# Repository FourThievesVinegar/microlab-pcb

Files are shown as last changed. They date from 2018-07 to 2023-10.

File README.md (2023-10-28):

# FTVC Microlab PCB

## NOTE: This project is deprecated. [The new version of the Microlab](https://github.com/FourThievesVinegar/solderless-microlab) uses a Raspberry Pi.

Four Thieves Vinegar Micro Lab

This is the printed circuit board hardware component for controlling the Four Thieves Vinegar Collective's Apothecary Microlab. It was built with Altium Designer v15 and sits mezzanine to the Raspberry Pi Zero.

## Building

To build your own Microlab PCB follow these guides:

[Ordering the PCB](docs/order-pcb.md)

[Ordering the PCB Components](docs/order-pcb-components.md)

## Interfaces

The PCB provides the following interfaces:

* 2 x 12 V Stepper motors
* 4 x Buttons for stepper motor control
* 4 x Limit switches
* 1 x DC motor controller (PWM)
* 3 x Relays
* N x DS18B20 temperature probes
* 2 x Raspberry Pi GPIO

## Electrical

### Power

The PCB is powered by a 12 VDC power brick. It will supply power to the Raspberry Pi Zero, stepper motors, stirrer motor, and temperature probes.

The power connector is a standard 2.10mm ID, 5.50mm OD centre-positive barrel jack connector (PJ-037AH).

Power consumption has yet to be measured.

### Stepper Motors

Drives two bipolar (four-wire) stepper motors with 12 V at 1.2 A max.

Stepper motor driver IC: TB6612FNG.

### Buttons and Limit Switches

Active-high. Includes pull-down resistors and debounce RC filters.

### DC Motor Controller

Supplies 12 VDC at 2 A max. Connected to a PWM pin on the Pi.

### Relays

Rated for 250VAC, 125VDC at 10 A max.

**WARNING:** If you are switching main's powered devices, be careful not to touch the exposed leads on the bottom of the PCB.

### Temperature Probes

Supports any number of DS18B20 temperature probes. Connected to the 1-wire pin on the Pi and includes the data-line pull-up resistor.

### Pi GPIO Pins

Two Pi GPIO pins, BCM0 (pin 27) and BCM1 (pin 28) are exposed along with 5, 12, 3.3 V and GND on a six pin header.

## Mechanical

The PCB is 100 mm x 50 mm with rounded corners.

The three M2.5 mounting holes are concentric with the Pi's. They are drilled to 2.75 mm diameter and provide 6 mm diameter clearance. The centre-to-centre horizontal and vertical distance is 58 mm and 23 mm. The holes' centres are 3.5 mm from their board edge.

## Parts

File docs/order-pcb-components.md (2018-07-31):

# Ordering the PCB Components

This document describes how to order the electrical components for the Apothecary Microlab PCB.

## Info

Cost is USD $30 - $35 + shipping from Digi-Key and takes one to two days to ship within North America.

Includes parts for one Microlab PCB. If you'd like to assemble more, multiply the quantities in the spreadsheet.

## Steps

### Download the BOM

Git clone or download this repository onto your machine.

Alternatively, you can just download the [outputs/microlab-BOM.xls](../outputs/microlab-BOM.xls) file directly from GitHub.

### Create a Digi-Key account

Go to [digikey.com](https://www.digikey.com/) and select your country / region on the top right.

Register to create an account.

### Upload the BOM

Once logged in, view your shopping cart on the top right.

Upload the microlab-BOM.xls file to the shopping cart.

Set the first part record to row two:

Digi-Key first record

Scroll to the right and assign the last three columns of the table to "Digi-Key Part Number", "Customer Reference" and "Quantity":

Digi-Key column options

Click "Add to new cart" and allow it to process your request.

### Order the parts

Review your cart and press the "Checkout" button. Enter your address and payment info.

Place your order, and you are done!

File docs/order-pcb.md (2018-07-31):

# Ordering the PCB

This document describes how to order the Apothecary Microlab PCB to be manufactured.

## Info

Cost is USD $2 + $20 shipping from JLC PCB and takes six days to manufacture and ship to North America.

Includes 10 Microlab PCBs.

## Steps

### Prepare the Gerbers

Git clone or download this repository onto your machine.

Zip all the files in the [outputs/gerbers](../outputs/gerbers) directory into a single archive. Ensure the files are at the root of the archive and not inside a sub-directory.

### Create a JLC PCB account

Go to [jlcpcb.com](https://jlcpcb.com/) and sign up for an account. We use them because they have a special offer of $2 for 10 PCBs and have been tested.

### Upload Gerber files

On the home page, select "Quote Now" for a 2-layer PCB.

Press "Add your gerber file" and upload the .zip file you created. After a short time, it will show a rendering of the PCB.

_Note:_ The bottom side of the render will be mirrored on the website, but not on the real PCBs.

Leave the PCB options on their defaults:

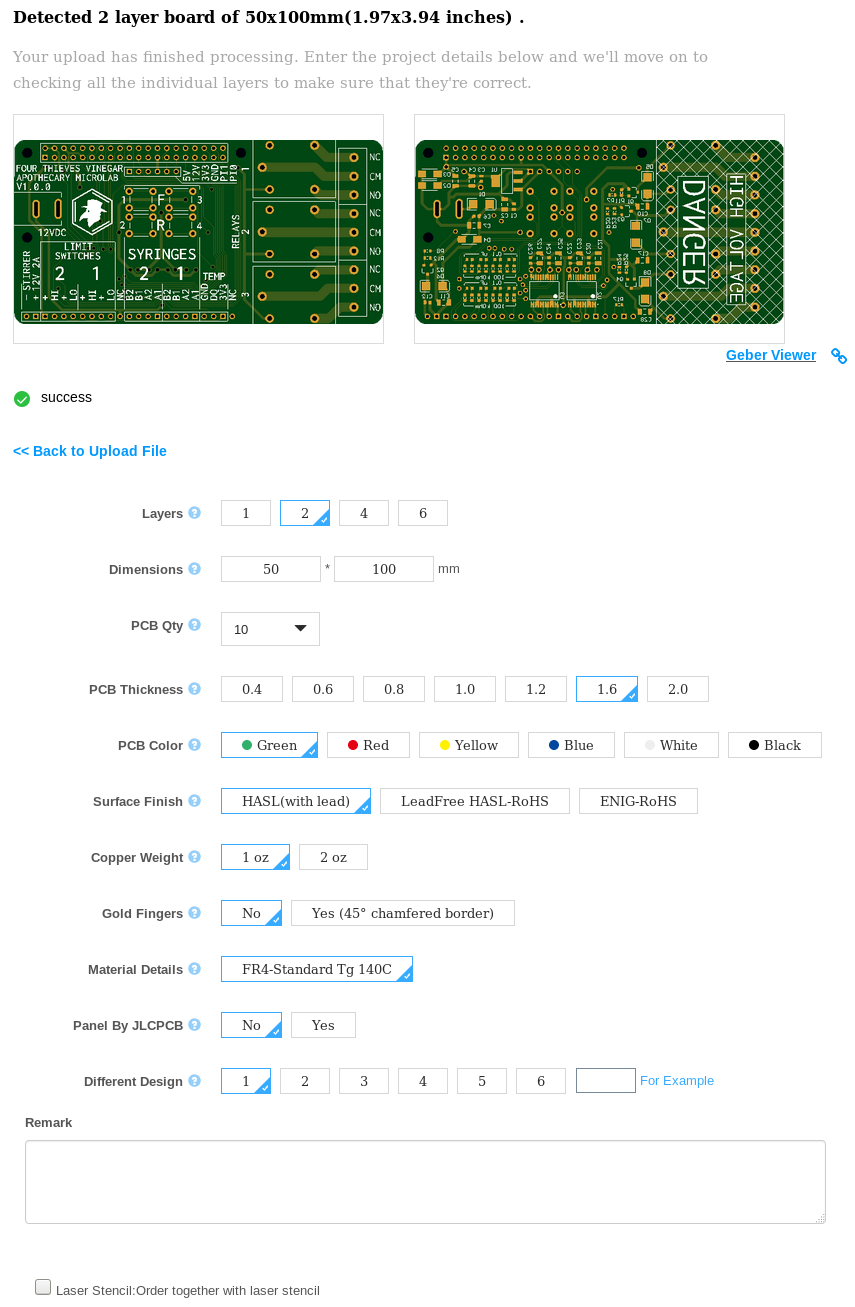
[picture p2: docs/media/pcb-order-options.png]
PCB order options


### Order PCBs

Press "Add to cart" and then "Checkout securely". Enter your address and payment info. Ensure "Pay Directly" is selected.

Place your order, and you are done!

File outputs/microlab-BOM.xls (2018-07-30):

From Altium |  |  |  |  |  |  |  | Actual BOM
Comment | Description | Designator | Digikey | Footprint | Quantity | Value | Voltage | Digi-Key Part Number | Reference | Quanitity
0.1 uF | Capacitor (Semiconductor SIM Model) | C1, C3, C6, C8, C9, C12, C13, C14, C15, C16, C18, C19, C20, C22, C24, C26 |  | 1608[0603] | 16 | 0.1 uF | 50 V | 478-5052-1-ND | C1, C3, C6, C12, C20, C22, C24, C26, “0.1 uF” | 16
10 uF | CL31A106KBHNNNE | C2, C4, C5, C7, C10, C11, C17, C21, C23, C25, C27, C28 |  | C1206 | 12 | 10 uF | 50 V | 1276-2876-1-ND | C2, C4, C5, C7, C10, C11, C17, C21, C23, C25, C27, C28 | 12
TSSA5U60 | Schottky Diode | D1, D5, D6, D7, D8 |  | SMB | 5 |  |  | TSSA5U60E3GCT-ND | D1, D5, D6, D7, D8 | 5
824501201 | TVS DIODE 20V 32.4V DO214AC | D2, D3, D4 | 732-9954-1-ND | 824501201 | 3 |  |  | 732-9954-1-ND | D2, D3, D4 | 3
PJ-037AH | CONN PWR JACK 2X5.5MM SOLDER | J1 | CP-037AH-ND | PJ-037AH | 1 |  |  | CP-037AH-ND | 12VDC | 1
G5LE-1-VDDC12 | RELAY GEN PURPOSE SPDT 10A 12V | K1, K2, K3 | Z3672-ND | G5LE-1-VDDC12 | 3 |  |  | Z3672-ND | RELAY 1, 2, 3 | 3
Header 20X2 | Header, 20-Pin, Dual row | P1 |  | HDR2X20-centred | 1 |  |  | S6104-ND | PI ZERO | 1
OSTTC032162 | Header, 3-Pin | P2, P5, P8 | ED2610-ND | OSTTC032162 | 3 |  |  | ED2610-ND | RELAY 1, 2, 3 | 3
Header 2 | Header, 2-Pin | P3 |  | HDR1X2 | 1
Header 8 | Header, 8-Pin | P4 |  | HDR1X8 | 1
Header 6 | Header, 6-Pin | P6 |  | HDR1X6 | 1 |  |  | S7039-ND | GPIO | 1
Header 3 | Header, 3-Pin | P7 |  | HDR1X3 | 1
Header 4 | Header, 4-Pin | P9, P10 |  | HDR1X4 | 2
AO3400A | MOSFET N-CH 30V 5.7A SOT23 | Q1, Q2, Q3, Q4 | 785-1000-1-ND | AO3400A | 4 |  |  | 785-1000-1-ND | Q1, Q2, Q3, Q4 | 4
100K | Resistor | R1, R2, R3, R4, R5, R6, R9, R10, R11, R12, R13, R14, R15, R16, R18, R19, R21, R22, R23, R25 |  | J1-0603 | 20 | 100K |  | A106046CT-ND | R11, R12, R23, R25, “100 kOhm” | 20
1K | Resistor | R7, R8, R20, R24 |  | J1-0603 | 4 | 1K |  | RHM1.0KDCT-ND | R7, R8, R20, R24 | 4
4.7K | Resistor | R17 |  | J1-0603 | 1 | 4.7K |  | P4.7KGCT-ND | R17 | 1
1825910-6 | SWITCH TACTILE SPST-NO 0.05A 24V | S1, S2, S3, S4 | 450-1650-ND | 1825910-6 | 4 |  |  | 450-1650-ND | S1, S2, S3, S4 | 4
LDL1117S50R | IC REG LINEAR 5V 1.2A SOT223 | U1 | 497-17240-1-ND | LDL1117S50R | 1 |  |  | 497-17240-1-ND | U1 | 1
TB6612FNG,C,8,EL | IC MOTOR DRIVER PAR 24SSOP | U2, U3 | TB6612FNGC8ELCT-ND | TB6612FNG,C,8,EL | 2 |  |  | TB6612FNGC8ELCT-ND | U2, U3 | 2
 |  |  |  |  |  |  |  | ED10568-ND | SYRINGES | 1
 |  |  |  |  |  |  |  | ED10567-ND | LIMIT SWITCHES | 1

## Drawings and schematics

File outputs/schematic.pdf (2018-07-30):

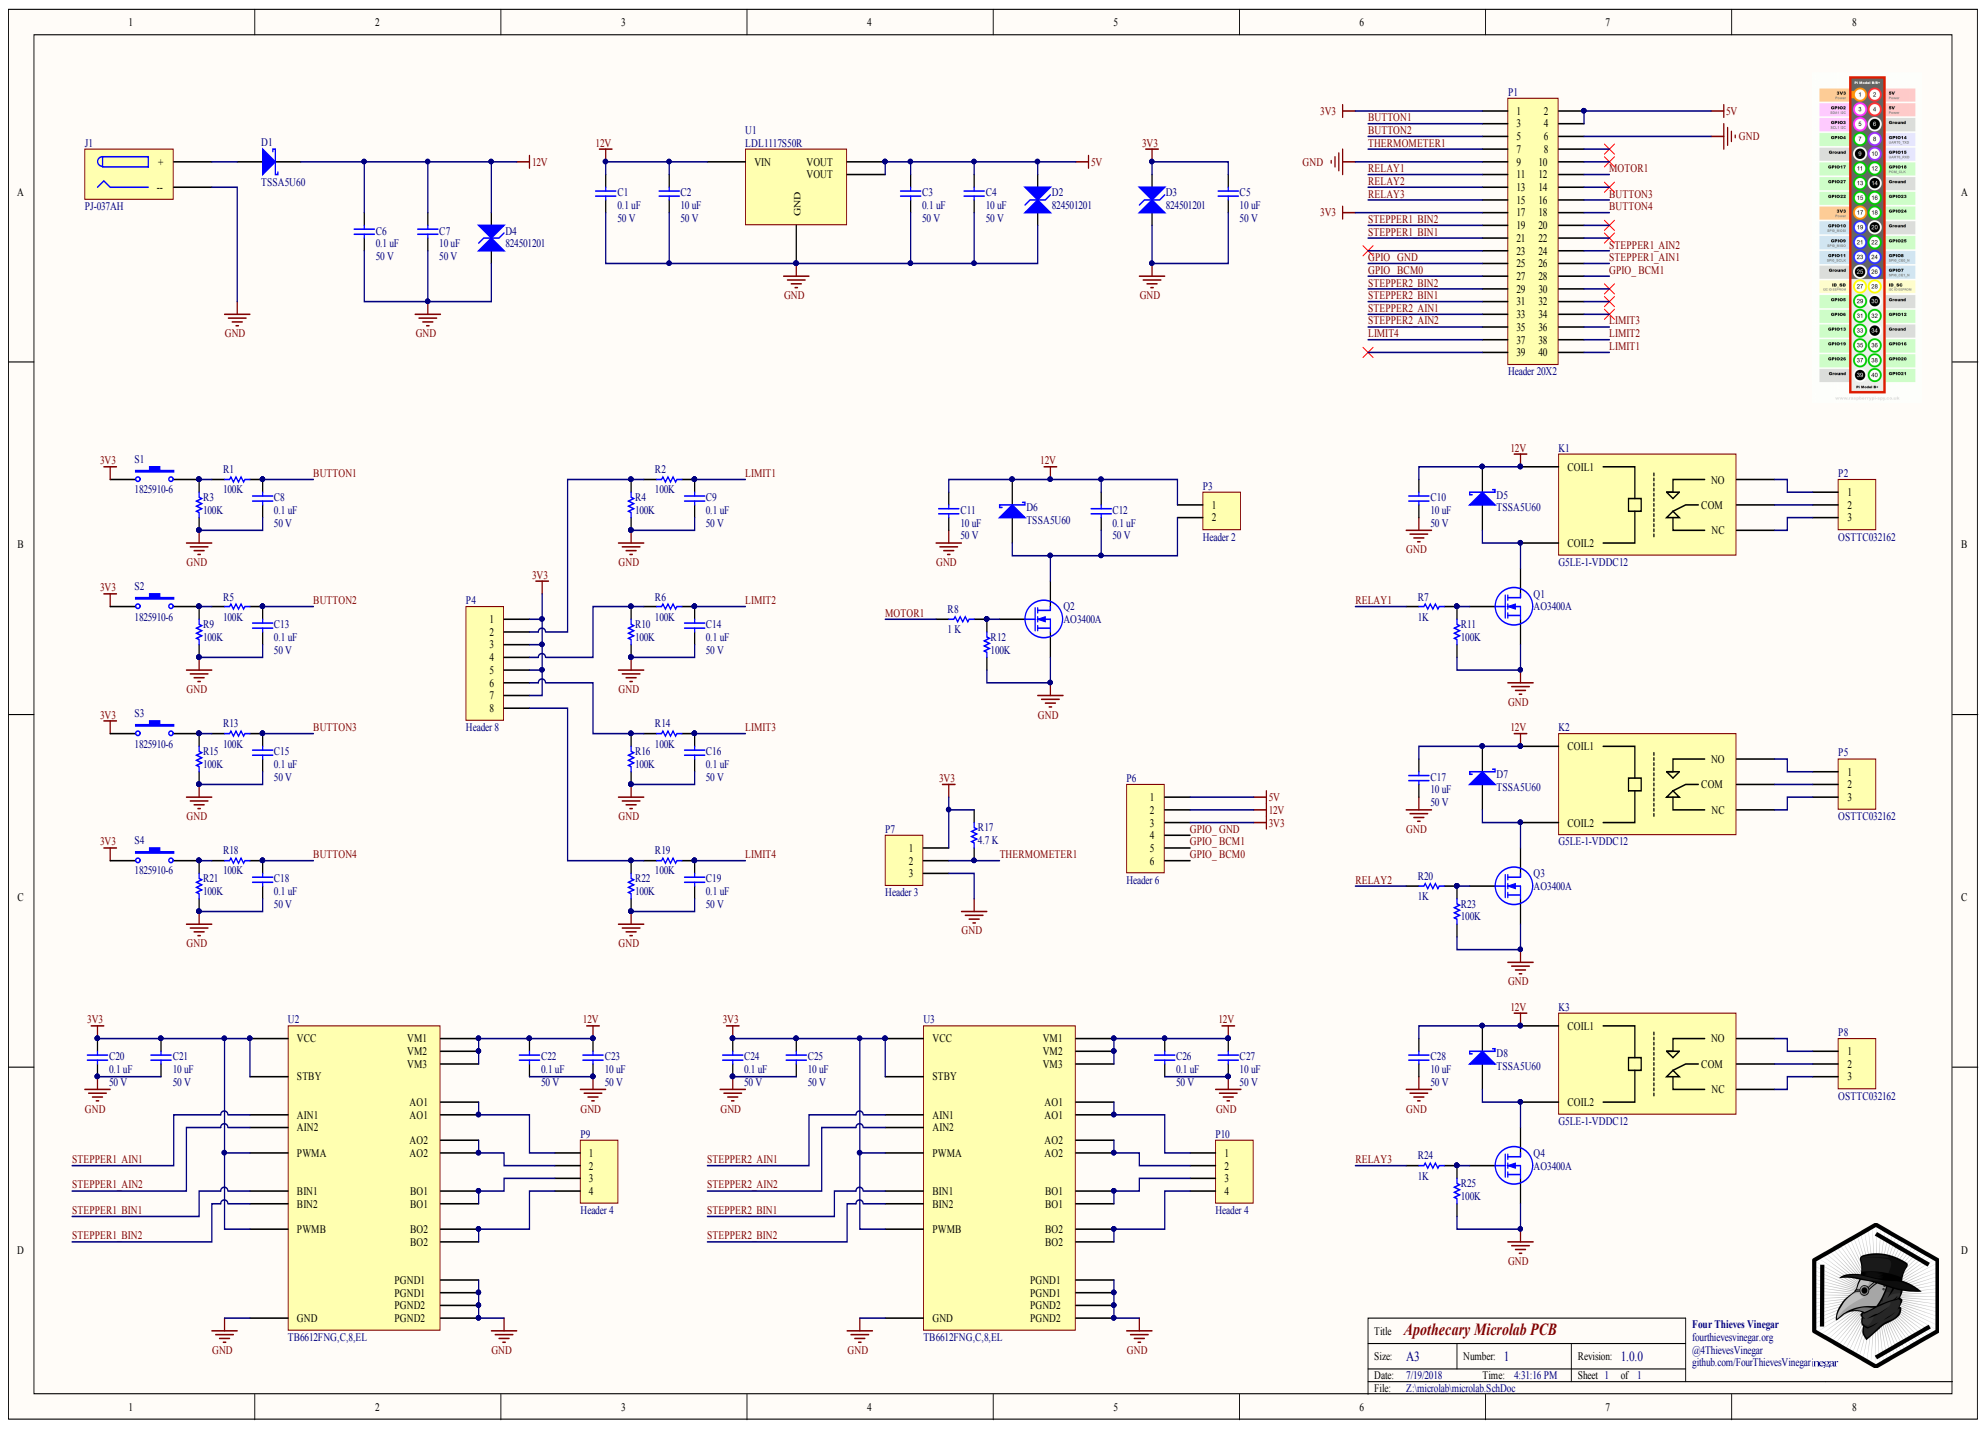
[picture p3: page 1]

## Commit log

2018-07-30 Add Microlab PCB design files
    [microlab.PcbDoc, microlab.PcbLib, microlab.PrjPcb, microlab.SchDoc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]
2018-07-30 Add Microlab PCB output files
    [microlab-BOM.xls, microlab.GBL, microlab.GBO, microlab.GBS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]
2018-07-30 Add PCB interface info to README
2018-07-31 Add info for ordering the PCB and components
